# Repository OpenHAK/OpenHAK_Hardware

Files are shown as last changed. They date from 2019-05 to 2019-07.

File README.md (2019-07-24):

# OpenHAK Hardware
## OpenSource Health Activity Kit Hardware Files

KiCad files for the beta OpenHAK boards. 

**Check the branches tab! There is a branch for the BioHacking Village Badge at DEFCON 27 and also a OSH Park Beta Tester branch**

### WARNING: Siblees don't exist!

Hi. Here you'll find everything that you need to make yourself your very own OpenHAK! If, that is, you have any spare [Simblees](https://www.digikey.com/product-detail/en/rf-digital-corporation/RFD77101/1562-1034-ND/5723430) lying around. Should you do have some Simblees that are just taking up space, then you're in luck! Simblees are very well trained to handle reflow with a hot air gun or toaster oven many, many times. Trust me, they are tough buggers. If you *don't* have any Simblees propping open your window or shimming up your wobbly cafe table, then you're out of luck... Or are you....?

## What's going on?

**O**pen**HAK** is an **O**pen source **H**ealth **A**ctivity **K**it. Right out of the box you can wear it on your wrist (or your ankle, if you're into that kind of thing) and start tracking your steps and heart rate with a mobile app. No kidding. All of it is open-source and ready to use, modify, and share. We *were* going to call it an **O**pen **S**ource **H**ealth **I**nformation **T**racker, but we don't want to confuse people.

## Who owns the data?

Data? What data? We don't own anything. We don't keep secrets from you, or try to distract you with shiny things while we stuff your data into our AI mattress monster. No. All the data is yours. YOU can delete it or share it or analyze it or whatever it. We don't care, just don't ask us for it 'cause we don't have it. It's yours and it gets stored on your phone, or tablet, or whatever you hack the OpenHAK to spit your data into.

## What's in the box

So glad you asked. Right now, we are engaging with our beta testers and the hardware has some features that we are excitedly happy to tell you about.

* BLE
	* Yes, it's a Simblee, but it's still a pretty awesome BTLE module that can do some incredibly cool stuff. We are supporting our very own OpenHAK Arduino board variant that is based on the the original Simblee board files. We've made it easy to create the .zip packet you need to upload new code over-the-air. Every OpenHAK comes preprogrammed with Nordic's DFU library installed, so you can write your own firmware and upload it over the air from your phone to your OpenHAK.
* BMI160
	* This multi-axis MEMS monster is what we're using to count your steps, and interface with your finger tapy tap taps. We are revealing full access to it's inner guts for you to transmogrify the OpenHAK into a gesture controller so you can control your monster robot to slay your adversary's monster robot(s) with a simple gesture.
* MAX30101
	* Yes, it's a MAX integrated heart rate sensor. In the BETA version we are using the MAX3010**1** variant. If you've ever used them they are super fun to play with. **We know.** It's not easy to get heart rate off of the wrist/ankle. It's not impossible, but it's hard. That's part of the reason why we're doing this, to see how an open-source community can come together and find creative ways to solve this among many problems.
* ACCESSORIES
	* We are breaking out a handful of pins (8 for the BETA version, 10 for the BioHacking Village Badge) that are user accessible. These are useful as an Arduino compatible program interface. Also, um, maybe driving an OLED display? To, maybe, let you know when your friend is texting you ('cause it's connected to your phone...)? It could also drive an ERM (vibrator, ahem) to provide haptic feedback about stuff. The point is that since it's open-source, it's up to you. We will put up PCB design guidelines and templates so that you can create the thing you want to wear on your wrist/ankle/ahem.

## What else

The board is fit with physical features that will capture pins from an 18mm watch band. 18mm is a standard watch band size so you can accessorize with watch bands to your heart's delight!

## And
We placed the MAX30101 sensor all by itself on the (recommended) skin side of the board. We did this to facilitate enclosure design. We have a prototype case (link) that performs well under reasonable circumstances (no, we haven't mountain-biked in a wintery mix with it yet...).

If you've gotten this far then you're not even halfway down! Keep mining this repo and, don't be shy, we're only an issue away!

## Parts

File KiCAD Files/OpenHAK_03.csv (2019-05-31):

Id | Designator | Package | Quantity | Designation | Manufacturer | Part Number | Alternate Part Number
 | BT1 | JST_SH_SM02B-SRSS-TB_02x1.00mm_Angled | 1 | Battery | JST | SM02B-SRSS-TB(LF)(SN)
 | C3,C5,C11 | C_0402 | 3 | 10uF | Murata | GRM155R60G106ME44J
 | C7,C1,C10,C15,C16 | C_0402 | 5 | 0.1uF | Yaego | CC0402KRX5R6BB104
 | C8,C2,C4,C6,C9,C12,C13,C14 | C_0402 | 8 | 1uF | Taiyo | JMK105C6105MV-F
 | D1 | CLMVB-FKA-CFHEHLCBB7a363 | 1 | Led_RGB_CA | Broadcom | ASMB-KTF0-0A306 | CLMVB-FKA-CFHEHLCBB7A363
 | D2 | C_0603 | 1 | D_Schottky | Comchip | CDBU00340
 | D3 | 0606_Bi-Color | 1 | Dialight_R_G_LED | Everlight | 18-225SURSYGC/S530-A4/E4/TR8
 | P1 | 1x8_SMT_F | 1 | CONN_01X08 | Harwin | M50-3140845
 | P2 | 10118193_microUSB | 1 | USB_OTG | Amphenol | 10118193-0001LF
 | R1,R2,R14 | C_0402 | 3 | 10K | Vishay | CRCW040210K0JNEDC
 | R13,R15 | C_0402 | 2 | 470R | Yaego | RC0402JR-13470RL
 | R5,R12,R17 | C_0402 | 3 | 100R | Yaego | RC0402FR-07100RL
 | R7,R8 | C_0402 | 2 | 1M | Yaego | RC0402FR-071ML
 | S3,S4,S4,S3,S3,S4,S1,S2 | C_1206 | 8 | Watch Pin | Stackpole | HCJ1206ZT0R00
 | U1 | RFD77101 | 1 | rfd_77101 | RFDigital | RFD77101
 | U2 | MAX3010x | 1 | MAX301_Series | Maxim | MAX30101EFD+
 | U3 | MLF-4 1mm x 1mm | 1 | MIC5365 | Microchip | MIC5365-1.8YMT-TZ
 | U6 | MLF-4 1mm x 1mm | 1 | MIC5365 | Microchip | MIC5365-3.0YMT-TZ
 | U4 | LGA_2.5x3 | 1 | BMI160 | Bosch | BMI160
 | U5 | SOT-23-5 | 1 | MCP73831 | Microchip | MCP73831T-2ATI/OT
 | U7 | X2SON8_1.4mm_x_1mm | 1 | TXS0102_LEVEL_SHIFTER_X2SON8 | Texas Instruments | TXS0102DQER
 | U8 | SOT-323_SC-70 | 1 | MAX809 | On Semi | MAX809SQ308T1G

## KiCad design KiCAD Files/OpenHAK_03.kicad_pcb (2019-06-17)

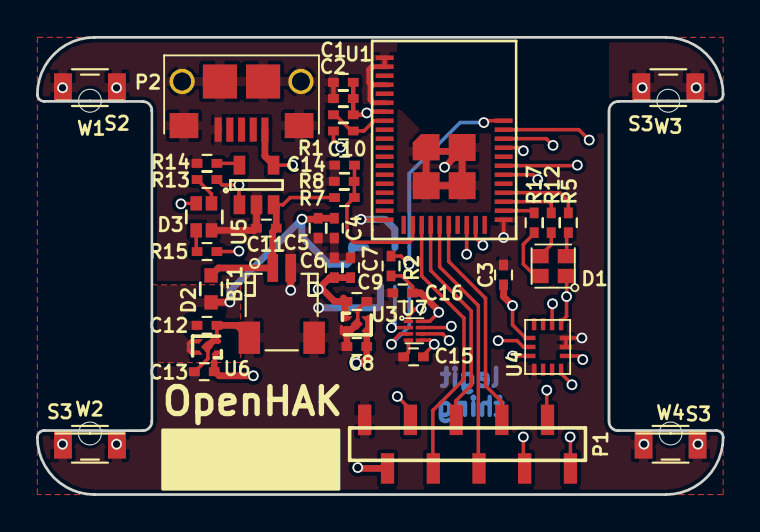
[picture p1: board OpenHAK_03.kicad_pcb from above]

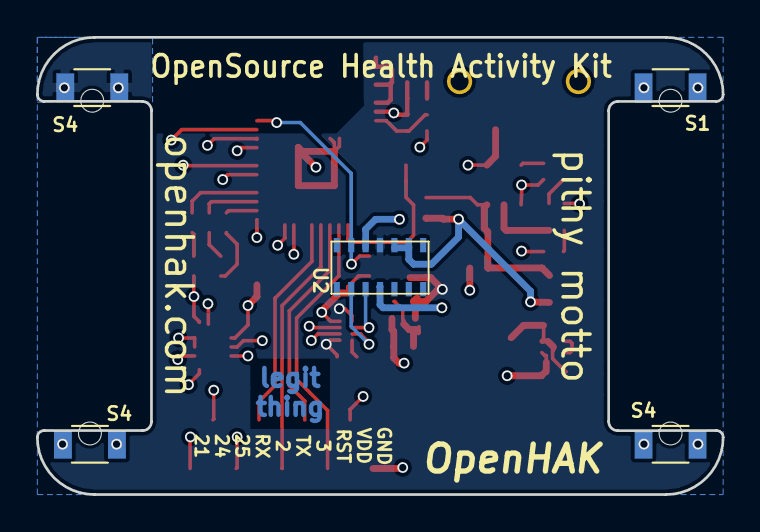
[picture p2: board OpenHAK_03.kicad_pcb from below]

Board: 4 copper layers, 38.1 x 25.4 mm, 51 parts (5 on the bottom side), 33 nets.

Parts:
BT1: Battery; JST_SH_SM02B-SRSS-TB_02x1.00mm_Angled
C1, C7, C10, C15, C16: 0.1uF; C_0402
C2, C4, C6, C8, C9, C12, C13, C14: 1uF; C_0402
C3, C5, C11: 10uF; C_0402
D1: ASMB-KTF0-0A306; CLMVB-FKA-CFHEHLCBB7a363
D2: D_Schottky; C_0603
D3: 18-225SURSYGC/S530-A4/E4/TR8; 0606_Bi-Color
P1: Harwin M52 Series; M52-Series_Harwin_SMT_10P
P2: USB_OTG; 10118193_microUSB
R1, R14: 10K; C_0402
R2: 4K7; C_0402
R5, R12, R17: 100R; C_0402
R7, R8: 1M; C_0402
R13, R15: 470; C_0402
S1, S2, S3, S3#2, S3#3, S4, S4#2, S4#3: C_1206
U1: rfd_77101; RFD77101
U2: MAX30100
U3: MIC5365-1.8YMT-TZ; MLF-4 1mm x 1mm
U4: BMI160; LGA_2.5x3
U5: MCP73831T-2ATI/OT; SOT-23-5
U6: MIC5365-3.0YMT-TZ; MLF-4 1mm x 1mm
U7: TXS0102DQER; X2SON8_1.4mm_x_1mm
W1, W2, W3, W4: Watch_Pin_50mil

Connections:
+1V8: C6.1, C7.2, C9.2, C15.2, U2.11, U3.1, U7.1, U7.5
/1V8_SCL: U2.2, U7.3
/1V8_SDA: U2.3, U7.2
/3V3_SCL: U1.28, U4.13, U7.6
/3V3_SDA: U1.27, U4.14, U7.7
/BMI_INT1: U1.40, U4.4
/BMI_INT2: U1.39, U4.9
/B_LED: R17.2, U1.31
/G_LED: R12.2, U1.32
/MAX_INT: R2.2, U1.41, U2.13
/PIN_2: P1.6, U1.24
/PIN_3: P1.4, U1.22
/PIN_21: P1.10, U1.36
/PIN_24: P1.9, U1.35
/PIN_25: P1.8, U1.38
/R_LED: R5.2, U1.33
/SIM_RST: C10.2, R1.2, U1.8
/SIM_RX: P1.7, U1.25
/SIM_TX: P1.5, U1.23
/V_BATT: BT1.1, C11.2, D2.2, R7.2, U5.3
/V_SENSE: C14.2, R7.1, R8.2, U1.21
GND: BT1.2, C1.1, C2.1, C3.1, C4.2, C5.2, C6.2, C7.1, C8.1, C9.1, C11.1, C12.1, C13.1, C14.1, C15.1, C16.1, D3.2, P1.1, P2.5, P2.6, P2.7, P2.8, P2.9, P2.10, P2.11, R8.1, R14.2, S1.1, S1.2, S2.1, S2.2, S3.1, S3.2, S3#2.1, S3#2.2, S3#3.1, S3#3.2, S4.1, S4.2, S4#2.1, S4#2.2, S4#3.1, S4#3.2, U1.1, U1.2, U1.4, U1.6, U1.19, U1.30, U1.42, U1.43, U1.44, U1.45, U2.4, U2.12, U3.2, U3.5, U4.1, U4.6, U4.7, U5.2, U6.2, U6.5, U7.4
unnamed: C10.1, P1.3
unnamed: D1.2, R17.1
unnamed: D1.3, R12.1
unnamed: D1.4, R5.1
unnamed: D3.1, R13.2
unnamed: D3.3, P2.1, U5.4
unnamed: D3.4, R15.2
unnamed: R13.1, R15.1, U5.1
unnamed: R14.1, U5.5
VDD: C1.2, C2.2, C3.2, C8.2, C13.2, C16.2, D1.1, P1.2, R1.1, R2.1, U1.7, U3.3, U3.4, U4.5, U4.8, U4.12, U6.1, U7.8
VPP: C4.1, C5.1, C12.2, D2.1, U2.9, U2.10, U6.3, U6.4

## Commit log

2018-02-01 Initial commit of OpenHAK beta design files
    Moving into v1 design of the OpenHAK hardware
    [OpenHAK.kicad_pcb, OpenHAK.sch]
2018-02-28 Added cap to VSENS to fix battery reading
    [OpenHAK.sch]
2019-05-31 Updated with latest files
    [OpenHAK.kicad_pcb, OpenHAK.sch, OpenHAK_03.csv, OpenHAK_03.kicad_pcb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]
2019-06-15 removed some stuff we don't need and made notes about changes to pcb
    [OpenHAK_03.sch]
2019-06-16 Major changes to the board layout
    took some things off, put some things on, and moved some things around
    [OpenHAK_03.sch]
2019-06-16 Cleaned up silk
    [OpenHAK_03.kicad_pcb, OpenHAK_03.sch]
2019-06-17 added to ignore
    [OpenHAK_03.kicad_pcb]
